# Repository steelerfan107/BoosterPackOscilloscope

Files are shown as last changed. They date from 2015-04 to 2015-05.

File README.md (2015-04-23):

# BoosterPackOscilliscope
An open hardware design sponsored by Texas Instruments to create a Oscilloscope BoosterPack for their LaunchPad series.

#Results

YouTube Videos of Current Version

https://www.youtube.com/watch?v=cYiwDeTmkGY
https://www.youtube.com/watch?v=qeyE9i_el2E
https://www.youtube.com/watch?v=waJ3gXQC8M0
https://www.youtube.com/watch?v=UX_YCJf1Lo4

#Design Files

Contains 
	- Software Files including the Energia Workspace and the Modified Screen Drivers
	- Hardware Files containing EAGLE files of the schematic and board designs. Also included are seperate sheets showing each subsystem.
	- BOM - Bill of Materials

#Reports

Contains
	- All of the reports for this project including
		Project Proposal - Initial project definition 
		Project Plan 	 - Initial schedule of project completeion 
		Decomposition 	 - A breakdown of each subsystem into circuits explaining why parts were used and how
		Final Reort	 - Outlines what worked well and what didnt

#Reserch Memos

Contains
	- Three memos looking into differant aspects of the project.

#Technical Sources

Contains
	- Datasheets of all major parts used

#Testing Plans and Data

Contains
	- Plans to test two subsystems and the results

#User Manual 
	- Contains how to setup project once the board is assembled and fabricated 

If you have any questions just email me at: eric.taylor.9090@gmail.com

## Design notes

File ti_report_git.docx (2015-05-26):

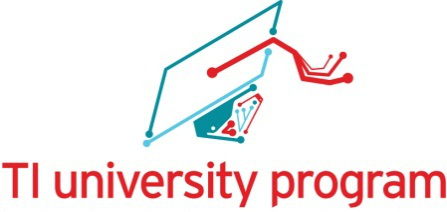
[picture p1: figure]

Oscilloscope BoosterPack (Low Cost) | Rose-Hulman

TI Innovation Challenge 2015 Project Report

Team Leader: | | Eric Taylor, taylorem@rose-hulman.edu
Team Members: | | Team Raymond Montgomery, montgora@rose-hulman.edu
Advising Professor: | | Mark Yoder, yoder@rose-hulman.edu
Video | | https://www.youtube.com/watch?v=cYiwDeTmkGY
Texas Instruments Mentor (if applicable): | | Trey German,treygerman@ti.com
Date: | | 5/11/2015
Qty. | List all TI analog IC and TI processor part number and URL | | 1) Explain where it was used in the project? 2) What specific features or performance made this component well-suited to the design?
2 | THS4121 | | This part was used for the Single-To-Differential conversion on the front end. Two were needed to get two channels. This was well suited because it ran of 3.3V and had the proper input range for the inputted signal and an adjustable common mode voltage to match with the LMH6882’s common mode voltage.
1 | LMH6882 | | This was used to have programmable gain on both of the channels. This was used because it has two channels on a single chip and had a wide range of gain settings which is useful for our application. The parallel bus also made it easy to control.
2 | OPA140 | | These were used to buffer the common mode voltage coming out of the ADC into the THS4121 and LMH6880. These were used because of the proper input range and we just were looking for the cheapest general purpose op amp possible since no frequency specs were needed.
1 | ADS5237 | | This was the ADC of the circuit used to sample both of the channels. It was used because of the fast sample rate of 65 MSPS and having a high 10 bit resolution. The 65 MSPS was around the limits of the EPI, and 10 bits was about our target when designing the front end. (Any more precision would be lost in the quality of the front end)
1 | TM4C1294NCPDT | | This was the microcontroller used to control our project. Since we are making a BoosterPack designed to attach to a Launchpad we picked the Connected LaunchPad because of the large amount of Pins and EPI bus capability,
3 | OPA890 | | These were used as an amp to offset the triggering signal and as a comparator to compare the signal to a specific trigger level. These chips were selected because of the low amount of skew and fast switching capabilities.
1 | TL7660 | | This was used as a negative source for the triggering circuit. This part was used because it was the cheapest part that did the intended job.

  - https://www.youtube.com/watch?v=waJ3gXQC8M0
  - https://www.youtube.com/watch?v=UX_YCJf1Lo4 https://www.youtube.com/watch?v=qeyE9i_el2E

GitHub: https://github.com/steelerfan107/BoosterPackOscilloscope

Project abstract (a short high level written description of the design and motivation behind project), 1,000 words max:

This project's objective was to design an oscilloscope BoosterPack that is compatible with TI LaunchPad series that is a low cost alternative to the typical desktop oscilloscope. This project was open source so anyone can learn from the hardware and software design and be able to expand upon them. The final product must be able to function as a reliable oscilloscope at an affordable cost to both hobbyists and students. As a low end design, the oscilloscope BoosterPack needs to push its cost down as much as possible while having the features of a typical oscilloscope. The main goal was to create a BoosterPack that has two measurement channels that can take a +/- 15V signal and has a bandwidth of 7MHz for under $50.

The design of this project had many aspects involving hardware and software. The hardware design consisted of three main circuits that we would need to design: sampling, front end, and triggering. The front end consisted of single to differential conversion along with adjustable gain to go into the sampling circuit. The sampling circuit consisted of an ADC to sample the signal from the front end and send it to the microcontroller. Finally the triggering circuit which takes a signal from the front end and compared it to a set level adjusted by the user and tells the microcontroller when to start sampling. All of this hardware will be on one board that is BoosterPack compatible and can be attached to the Connected LaunchPad. This allows for a display to be attached on top of this BoosterPack to display the signals. For this specific project we used a premade LCD BoosterPack and SPI controllers.

The other aspect was the software to control the device. For this we used Energia for the development and contained four parts. The first part was voltage and time deviation control. This was just done using the on board LaunchPad user buttons. The next was the amplifier control which was also just GPIO control. The next was the display drivers which were adapted from C drivers that came with the premade BoosterPack. Finally the sampling control with consisted of EPI, uDMA, and some other general code. The EPI was used to read in the 20 bit (both channels) quickly and the uDMA was used to store them in memory. Then two buffers were made to store the split samples and to determine if a certain samples changed positions on screen to keep screen refreshing to a minimum. However for our project we could not get the uDMA to work so we used timer interrupts to control how fast we took in samples. This greatly reduced the bandwidth of what we could measure, but since this project is open source and on GitHub there is the opportunity to add this feature in later.

## Table of Contents

## List of Tables and Figures

Figure 1. Primary Stakeholders and Features………………………………………………………………………………5

Figure 2. Domain Diagram ………………………………………………………………………………………………………….6

Figure 3. Logical Architecture………………………………………………………………………………………………………7

Figure 4. Front End Subsystem…………………………………………………………………………………………………….8

Figure 5. Trigger Level Subsystem………………………………………………………………………………………………..9

Figure 6. Sampling Subsystem……………………………………………………………………………………………………...9

Figure 7. Software Subsystem……………………………………………………………………………………………………..10

Figure 8. 50mV sine at (100kHz, 1MHz, 10MHz) (Top – Input to PGA, Bottom – Output of PGA).. 11

## Project Description

The project was to create an oscilloscope BoosterPack for TI’s Launchpad series which had the following features: two measurement channels, hardware triggering, user control, 6.5 MHz bandwidth, and +/ 15V input swing for all under $50. The reasoning behind the selection of these features can be seen below. In our final product we were able to accomplish most of what was needed but not all. The BoosterPack did have two working channels and a hardware trigger for under $50, however the software could not sample fast enough to get the 6.5 MHz bandwidth and adjustments are needed on the front end to get a full +/- 15 V input swing. The final board we made had a 200 kHz bandwidth and +/- 1.5V input swing.

2.1 Description of the Primary Stakeholders and Features

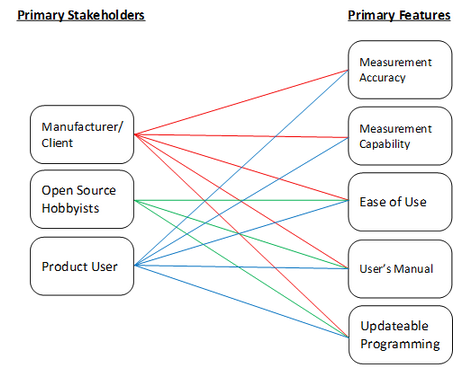
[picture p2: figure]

Figure 1. Primary Stakeholders and Features

The final product which consists of our physical circuit, the code that runs it, and the open source material all of which are determined by the primary stakeholders and features of our system as seen in Figure 1. The client, TI, provided this project submission and therefore cares about all the deliverables they requested. Anyone who uses the oscilloscope BoosterPack wants a functional final product and would want to reference the open source material for debugging errors and exploring the design of the product. Those who do own the product (like hobbyists and other recreational researchers) can still view the open source materials for studying circuit and code designs. The remaining features describe the actual function of the oscilloscope BoosterPack. ‘Measurement Accuracy’ and ‘Measurement Capability’ are distinct and necessary features for the final product. The accuracy describes the how well the oscilloscope BoosterPack’s measurements are to the actual signal being measured, while capability is a necessary step in determining signal accuracy because we need confirm that the data displayed on the oscilloscope is measurement data. Since the program on the circuit’s microcontroller can be changed, the user can see how making changes to the program can affect the operation of the oscilloscope and other programs can be loaded onto the LaunchPad so it can be used for different projects. As the project becomes easier to use, the user enjoys using the oscilloscope BoosterPack more which is why ease of use is a primary feature.

2.2 Description of the Solution

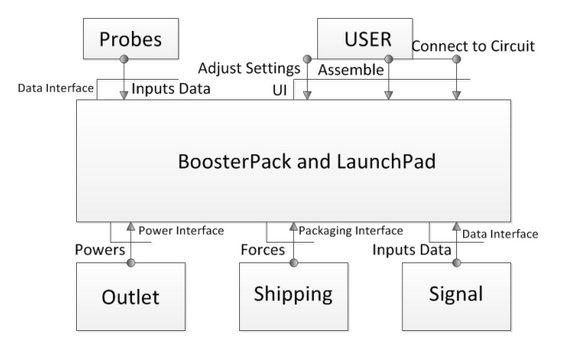
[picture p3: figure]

Figure 2. Domain Diagram

In Figure 2 the domain model of the project is presented. In this model the outside actors of the system are identified along with their interactions with the system. The first actor are the probes that are used in conjunction with the system. This directly related to measurement accuracy, ease of use, price limit, and measurement capabilities. The probes are what connects the signal to the circuit and have characteristics like input impedance and signal attenuation. These can effect what type of signal that could be measured and how accurate the system can be. The probes are also a separate component to reduce cost of the final package, and the user can use ones to their specification. For the final board design any BNC probe could be attached to measure signals. However when the 10x setting is used the signal does not go through. Further research is needed to figure out why this happens.

The next outside actor is the user which adjusts the settings, assembles/updates, and in general uses the scope. This directly relates to the ease of use, instruction manual, measurement capabilities, and price limit. The user needs to be able to operate the scope with ease, and should have a similar interface to other scopes on the market. This coincides with the user manual which explains the use of the scope to the user. Finally the user wants to be able to buy the product at a reasonable price given the performance the scope has. This was satisfied using buttons that came attached to the LaunchPad and a potentiometer attached to the BoosterPack. These controls allowed the user to adjust time and voltage per deviation, and also adjust the trigger level. Using controls that came with the LaunchPad also reduced the total cost of the board.

The next outside actors are outlet which directly effects power consumption, shipping which involves how the product is packaged, and the signal which related to accuracy and capability. The outlet determines how much power the scope can use. For power the final board can be powered by any micro usb source including portable battery packs. The shipping of the product relates the manufacturability and how the product is packaged. This was accounted for in the hardware design of the board. Finally the signal shape, size, and characteristics need to be known so the scope can be made to measure the variety of signals that it needs.

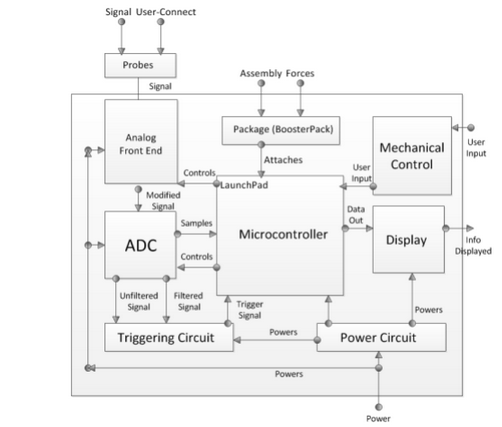
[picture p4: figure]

Figure 3. Logical Architecture

In Figure 3 we see the logical architecture of the system which describes how the scope will respond to the outside actors and shows how the system will function in general. Following the flow of the signal first comes the analog front end which accepts the signal from the scopes and proceeds to attenuate/amplify the signal, apply the proper common mode voltage, and make it differential. The signal is also put through a filter to reduce high frequency noise. The signal then proceeds to the ADC where it is sampled and then read into the memory of the microcontroller. The microcontroller the uses these samples and based on the user input displays the signal on a LCD screen.

The front end involves many parts, first of which is the THS4121 which does the single to differential conversion. This part was a cheap general part that is able to handle +/- 1.5V swings which was appropriate because we planned 10x probes working with the board which they did not. With 10x probes the +/- 1.5V swing would be enough for a +/- 15V input. This part also had the necessary bandwidth to handle 10 MHz signals.

The next part used was the programmable gain amplifier, LMH 6882. This part was first suggested by the client and worked well for our purpose. This amplifier has up to 25dB gain allowing for the measurement of small signals. This part also had two channels which reduced the part count on the board reducing cost.

Next came the sampling system or ADC. The ADC chosen was the ADS5237. This part had a sampling rate of 65 MSPS which allowed the measurement of signals up to 7MHz assuming the industry guideline of having 10 samples per period to have a good measurement on a signal. It also was selected because it had two channels which reduced part count and was relatively cheap compared to other ADCs that were up for consideration. Finally it had 10-bits of resolution which the client stated he wanted in the planning process.

The microcontroller which takes in the samples was satisfied using the Tiva C connected LaunchPad from TI. This board was needed because of the extra pins that were included which were needed to satisfy all of the requirements. This board also had EPI (External Peripheral Interface) which was a parallel bus that was needed to receive the 20-bit data signal for both channels at appropriate speeds.

Other blocks include the triggering circuit which takes in the filtered and unfiltered signal and tells the microcontroller when to start sampling based on a desired trigger level. This was done using cheap general purpose op-amps because of their low cost, and had satisfactory bandwidth for our features. The power circuit takes in the power from the outlet or USB and provides the microcontroller and the circuit with power. The power circuit was on the LaunchPad itself and no further circuitry was needed. The package block includes how it has to be manufactured to be able to interact with the Launchpad. This will be done by following BoosterPack templates and specifications. Finally the mechanical control which includes buttons which are on the Launchpad and a potentiometer which is on the BoosterPack.

Finally the display requirement was satisfied by an external BoosterPack made by a third party. This allowed us to focus on other features while satisfying a requirement at low cost. A simple 2.2” LCD controlled by SPI was used because of its low cost and simplicity to control.

This solution is able to deal with all of the major features which includes measurement accuracy, ease of use, measurement capabilities, updateable programming, and user manual. The measurement accuracy and capabilities are determined by the front end and ADC. Ease of use is taken care of by the mechanical control, display, and probes. However it couldn’t fully handle the features because the software wasn’t able to take in samples fast enough. The hardware could handle this requirement but software could not. Other than this detail the hardware selected was able to satisfy all of the requirements

## Hardware Design

### Front End

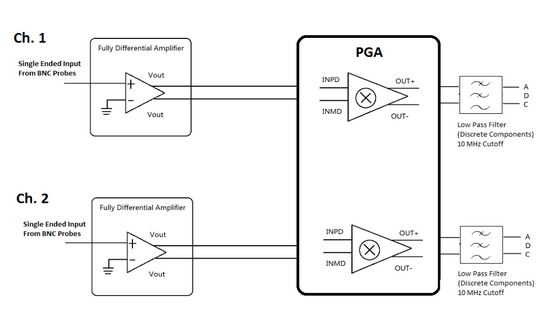
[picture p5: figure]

Figure 4. Front End Subsystem

For the Analog Front End, there is a BNC probe inputting the single ended signal. The reason we want the probes is to attenuate the signal by 10x and give the input impedance of 1MOhm. This is done because looking into the buffer there is a known high impedance of 1 Mohm and known attenuation.

Next, we have a fully differential amplifier (THS4121). Because the programmable differential amplifier requires two differential inputs, so we use the THS4121 to transfer the single signal to two differential input signals.

Last we have the dual channel differential PGA (LMH6882). The PGA Amplifies small signals so the ADC can measure the signals with proper resolution. This PGA is controlled by the microcontroller through parallel logic telling how much gain the signal need.

Finally there is a low pass filter to get rid of any noise to the ADC with a cutoff frequency of about 10 MHz.

### Triggering Circuit

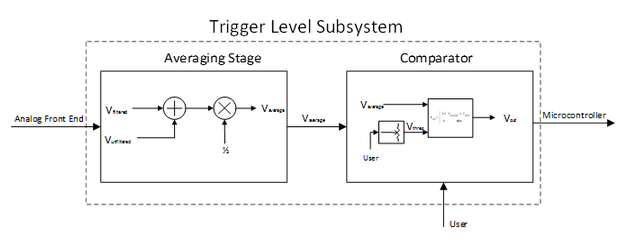
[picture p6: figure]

Figure 5. Trigger Level Subsystem

After a channel receives a signal. The Analog Front End scales the signal down so the op-amps in the Triggering Circuit can manipulate the input signal within the supply voltages. The user controls the potentiometer with a knob, or a similar control structure. The output of the Triggering Circuit is an array of logical values based on the sampling rate of the microcontroller and if there is one logical high in the array then the waveform is displayed. Logical high is an output of 5V and a logical low is an output of 0V

### Sampling Subsystem

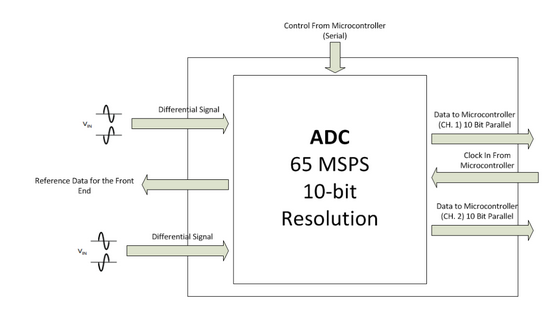
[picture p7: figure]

Figure 6. Sampling Subsystem

For our circuit we are going to use the ADS5237 ADC from TI. This chip is a dual channel, 10-bit resolution ADC that can sample at 65 MSPS. This will enable us to measure signals up to 6.5 MHz. This part has a listed use case for test equipment so that also gives reassurance it would be good to use in this case. The chip requires a clock signal from the microcontroller to tell it when to sample, and the data is sent back to the microcontroller over two 10-bit parallel lines. The analog signal coming in comes from the ADC and needs to be a differential signal within 0 to 2 V peak to peak.

Our ADC will not need serial control for now so it is disabled in the schematic for now.

## Microcontroller and Software

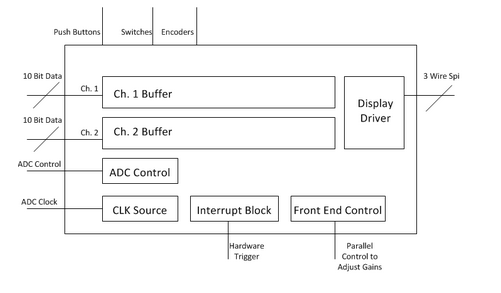
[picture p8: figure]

Figure 7. Software Subsystem

The microcontroller is the center of the project and will hold all of the software. We are using the Tiva C microcontroller that comes on the Connected series of Launchpad. The microcontroller is responsible for taking in the sampled data through an EPI (External Peripheral Interface) bus and storing it into a buffer after the trigger interrupts the microcontroller.

Knowing things such as voltage per division and time per division shown on the screen it will also control the sampling rate through increasing/decreasing the clock frequency to the ADCs. It will also control the amplification through the programmable gain amplifier which is a simple parallel interface.

The microcontroller also takes the user input from mechanical controls such as the push button, rotary encoders, and slide switches, and displays data on a LCD display which it will connect to through the built in SPI drivers.

### Testing Methids

Much of the formal testing of the project involved testing spate subsystems of the project. The first subsystem tested was the analog front end which was our black box testing.

For the black box testing we wanted to confirm the input requirements to the scope. This includes features like how high frequency of a signal can be inputted to the scope, and how large of a signal. This testing revolved around the front end because that is what takes the input signal and delivers it to the ADC for sampling.

For the setup of this testing the final board was made so a scope probe can take an input signal and there were testing wires soldered to the output of the analog front end right before the ADC. This allows us to see when a certain signal is inputted that the signal gets to the ADC correctly to be sampled. Here we are mostly looking for shape because depending on the settings of the programmable gain amplifier the true amplitude is unknown and is only known to the microcontroller which provide the correct gain factor to the samples. For the sake of this testing the lowest settings of gain were used for the programmable gain amplifier.

To start testing the functionality was confirmed with a 50mV input which is reality simulates a .5 V input because of the 10x probes (probes used were set at 1X). At 50 mV a sine wave was put through at 1kHz, 100kHz, 1MHz, and 10 MHz in addition to a square wave at 1MHz and a ramp wave at 200kHz. Again here we want to confirm the correct shape going into the ADC.

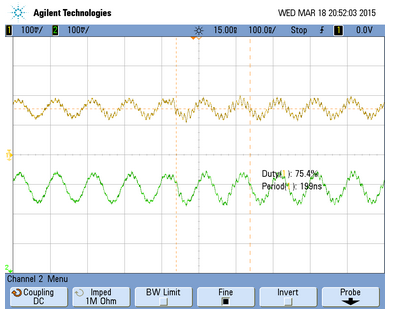
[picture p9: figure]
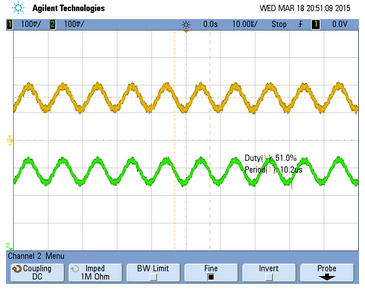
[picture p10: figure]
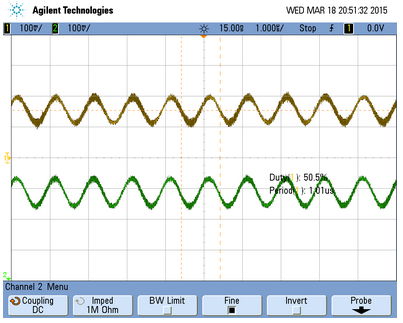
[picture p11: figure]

Figure 8. 50mV sine at (100kHz, 1MHz, 10MHz) (Top – Input to PGA, Bottom – Output of PGA)

Here is an example progression of the testing for the analog front end. In the above figure we specifically looked at small signals going into the front end and looking at what the ADC would see. Many configurations of this test were done at different frequencies and shapes but showing all would take too much space. Alongside this test our group also tested the triggering circuit individually.

For full system testing we assembled the oscilloscope and used it like anybody else would. We testing different shape, sizes, and frequencies of signals going into the scope. When we inputted a signal we tested what the screen was displaying. Many of these tests can be seen in the video and typically involved visual testing. Since our group ran out of time to finish the project in its entire little formal testing was done on the final system, it was mostly visual and user tested. The testing did go over well and showed what we got done worked, however it also did show what could be added to this project to make it better and where the shortcoming were. In the end we were able to input a +/- 1.5V signal up to 200 kHz, both channels were working, had adjustable voltage/time scaling, and had an adjustable hardware trigger. Fixes and further steps could be seen in the recommendations section.

### Conclusions

In the end our group was able to get the core functionality working along with many features such as the controllable trigger level and adjustable time/voltage scaling. It did fall short of the expected goals however. The Brightside is that small additions to software such as uDMA will improve the sampling speed, and addition of a selectable attenuator could improve input amplitude range.

### Future Work

Our project has fallen short of its expectations and its goals. The hardware is capable of handling the range of input signals (frequencies up to 7MHz) but the software can’t handle samples fast enough. A micro DMA method in software would help to handle samples faster and enables the oscilloscope BoosterPack to appropriately handle and display the higher frequency signals by writing the samples directly to memory when they are received. The software also doesn’t dynamically change the gain of the PGA to amplify smaller signals. However the control signals to do so are in hardware. More software would have to be added to allow the oscilloscope BoosterPack to measure the range of signals that we designed for. Finally adding a selectable attenuator to the front end would allow the hardware to accept larger signals. These recommendations would help the project to better meet the stakeholder features for Measurement Accuracy. Overall the core functionality works, meeting the Measurement Capability, Open Source Material, Ease of Use, and Updateable Programming features, but adding more software would allow the board achieve all its goals, and adding some hardware and software could help the project to meet these goals.

### Resources and Bibliography

Annotated List of Research Memos

[1] Yaohui Wang, Research of Analog Front End Design. October 7, 2014.

Description of the purpose and operation of an analog front end and looked into characteristics our group should look at when making our analog front end.

[2] Eric Taylor, Hold-Off Triggering, September 28, 2014.

A description of what hold off triggering is and how it works. This provided understanding of an oscilloscope feature that could be put into the scope at a later date.

[3] Raymond Montgomery, Oscilloscope Triggering. October 15, 2014.

This provided research into how our project will handle the triggering in hardware and gave understanding into which parts we should use and the general circuit subsystem that had to be made. This deals more with triggering hardware whereas the previous memo is software triggering features.

Annotated Biblliography

[1] I. King , High Performance Analog Front Ends, Analog Edge, Vol. IV Issue 1.

This source was used when the group didn’t have a good understanding of the purpose of an analog front end, and what characteristics of one made it a high performing one. This provided characteristics for the analog front end that our group could shoot for and design around.

[2] Microchip Technology Inc. Non-Inverting Summing Amps August 25, 2014. [Online]

This webpage explains the operation of amplifier circuits that sum signals together. This is useful in the triggering circuit to sum together the filtered and unfiltered signals.

[3] Circuits Today. Voltage Comparator. November 25, 2011. [Online]

This article was used to explain the user of voltage comparator circuits used in the triggering subsystem of our design.

[4] EEVBlog. Oscilliscope Trigger Holdoff Tutorial. March 29, 2011. #159 [Online]

This video provided understanding of holdoff triggering and how we could add it as a feature in our final scope.

[5] Texas Instruments. Oscilloscope Solution. [Online]

This is a compilation of resources by Texas Instruments that describes solutions and systems needed to make an oscilloscope. This was useful to learn all the systems we needed for our final project.

## Appendix

Note: All files and code on GitHub at steelerfan107/BoosterPackOscilloscope under Design Files

### Critical IC BOM

Part Value Device Package

-5V_SUPPLY TL7660_D_8 TL7660_D_8 D8

AVERAGER OPA890_DBV_6 OPA890_DBV_6 DBV6

COMPARATOR OPA890_DBV_6 OPA890_DBV_6 DBV6

OFFSET OPA890_DBV_6 OPA890_DBV_6 DBV6

U$3 LMH6882 LMH6882 WQFN-36-NJK

U1 ADS5237_PAG_64 ADS5237_PAG_64 PAG64

U2 THS4121_D_8 THS4121_D_8 D8

U3 THS4121_D_8 THS4121_D_8 D8

U4 OPA140AID OPA140AID SOIC127P600X175-8N 11MHz JFET Op Amp

U5 OPA140AID OPA140AID SOIC127P600X175-8N 11MHz JFET Op Amp

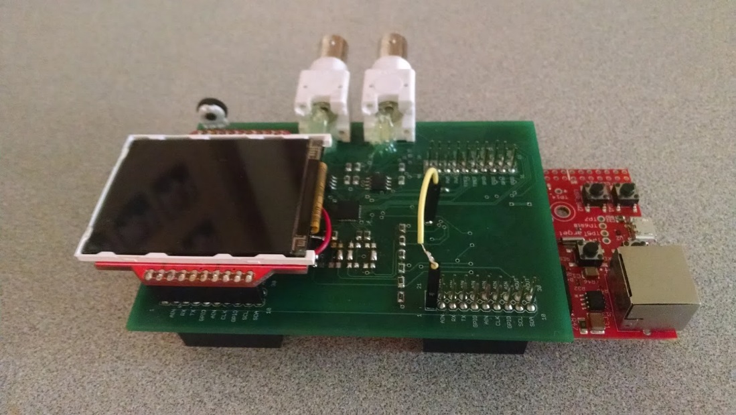
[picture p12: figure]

# TI BoosterPack Oscilloscope

User Manual 1.0

Eric Taylor and Raymond Montgomery | Rose-Hulman | Texas Instruments | Spring 2015

# Purpose

The purpose of this user manual is to help you get started setting up and getting familiar with the project. This assumes that you have the board already constructed from the board files on GitHub using the BOM also on GitHub. This will also include how to improve upon this project and traverse the files on GitHub .

# Table of Contents

Hardware Set-Up 3

- Color LCD Modifications 3
- Oscilloscope Board Jumper and Passive Filter 3
- Tiva C Connected LaunchPad 4

Software Setup 4

Usage of the Scope 5

TODOs 5

GitHub 5

# 1.0 Hardware Set-Up

To set up the hardware you need three things:

  - 2.2" Color LCD BoosterPack Kit by RobG
  - A Fabricated and Populated Oscilloscope PCB
  - Tiva C Connected LaunchPad

## 1.1 Color LCD Modifications

To make use of the EPI interface a small modification had to be made to the LCD BoosterPack hardware. You have to make sure neither jumper is soldered on the D/C pin, and then attach a wire to the middle pad and connect it to pad JP5. A picture showing this is below.

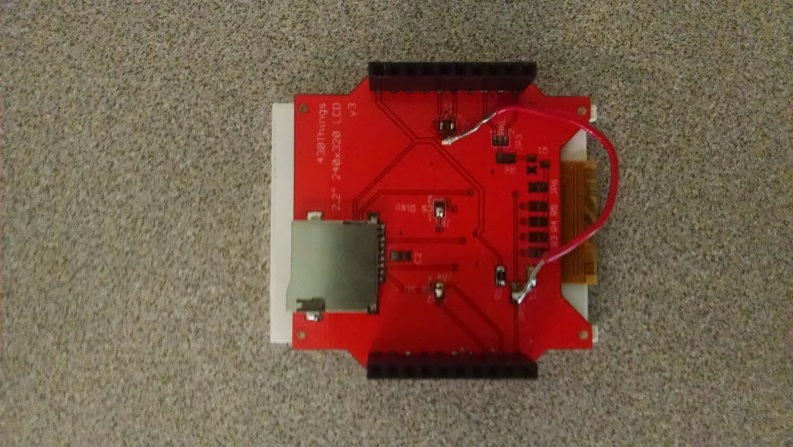
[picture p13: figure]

## 1.2 Oscilloscope Board Jumper and Passive Filter

For the purposes of debugging a pin was left exposed on the ADC for this first revision. Next revisions should connect this pin to the standard LDD for the ADC. (Connect VDRV to VDD in the EAGLE files). This jumper is necessary to power the ADC. A typical female-to-female jumper was used. A picture showing it is seen below. (The Yellow Wire). Also leave passive filter disconnected and solder the cap connections so the signal can continue through. More explanation in TODO.

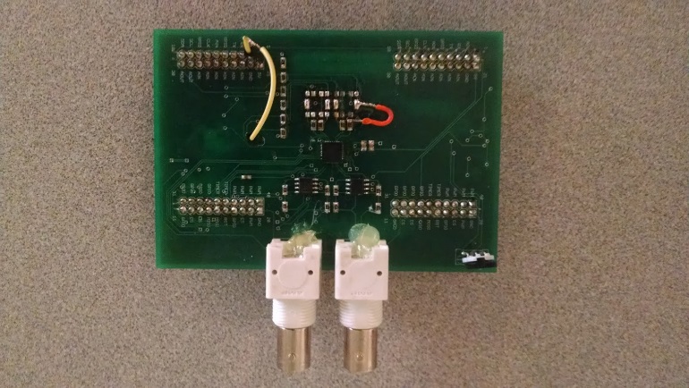
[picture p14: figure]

*Note - Orange Wire is there because of mistake while soldering

## 1.3 Tiva C Connected LaunchPad

No modifications should be needed. Make sure jumpers are connected like below.

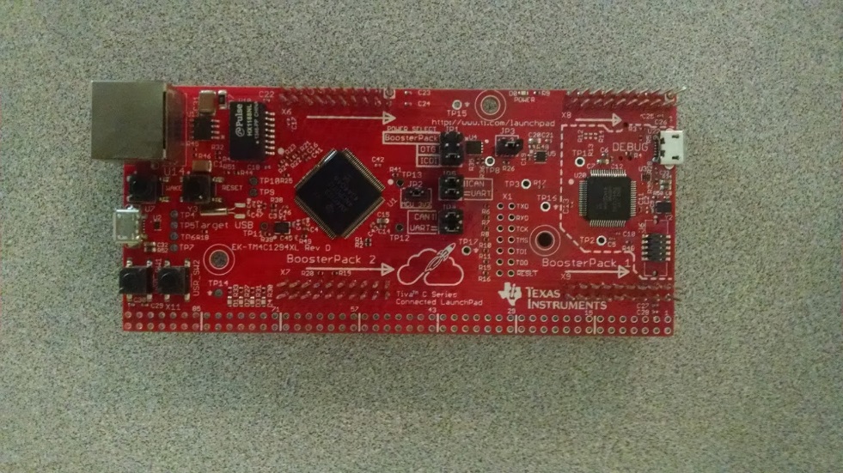
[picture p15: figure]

Once all hardware is setup, you can attach all of the pieces as seen on the first page.

# 2.0 Software Setup

Four things are needed for the software setup.

  - Energia w/ Tiva C Drivers
  - Senior_Project_Main.ino (on GitHub under Software Code)
  - Screen_ILI9340_Library.cpp/h

Minimal Setup is needed. First download Energia and put the screen driver and header files in the following path. (Note: The drivers are edited from the original online to account for the one pin being moved across the board.)

..\energia-0101E0013\hardware\lm4f\libraries\

Then open Senior_Project_Main.ino and select Tiva C tm4c129 as the board, Finally compile and run.

# 3.0 Usage of the Scope

  1. To use the scope you can use any BNC connector or 1x probe. However 10x probes did not work when tested with the system. Connect probes up like a typical scope. For this revision you can only trigger of one channel. (BNC away from Screen).
  2. Only signals from +/- 1.5 can be inputted at the end of the probe.
  3. Power can be supplied through any micro USB source. Portable battery or laptop will work.
  4. The trigger level can be adjusted using the potentiometer. Then the voltage per deviation and time per deviation can be adjusted using the two user buttons on the LaunchPad.

Note: The GUI is still in its early stages and can be improved upon.

# 4.0 TODOs

This section contains improvements that can be made on this project and steps to continue its development.

  1. Switch BNC connections so that they are vertical. They are currently unstable.
  2. Add buffer to front end so that 10x probes cannot load circuit.
  3. Add switchable attenuator to front end.
  4. Add uDMA to software to collect samples faster and be able to achieve full 7 MHz bandwidth . Currently a timer interrupt is used and the bandwidth is about 200kHz.
  5. Put 10MHz flat pass band active filter instead of current passive filter.

# 5.0 GitHub

On GitHub you can find a directory listing on the front page giving explanation to the file directory and source files. GitHub at steelerfan107/BoosterPackOscilloscope

### Schematics

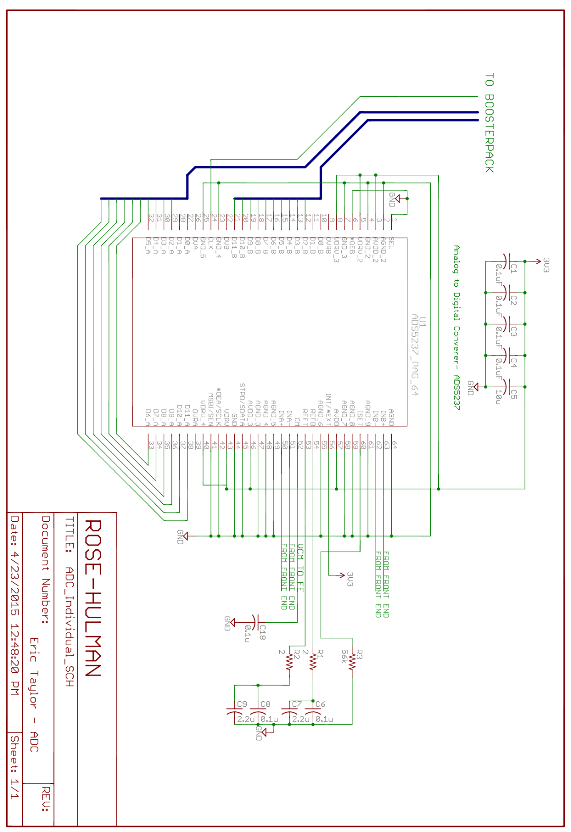
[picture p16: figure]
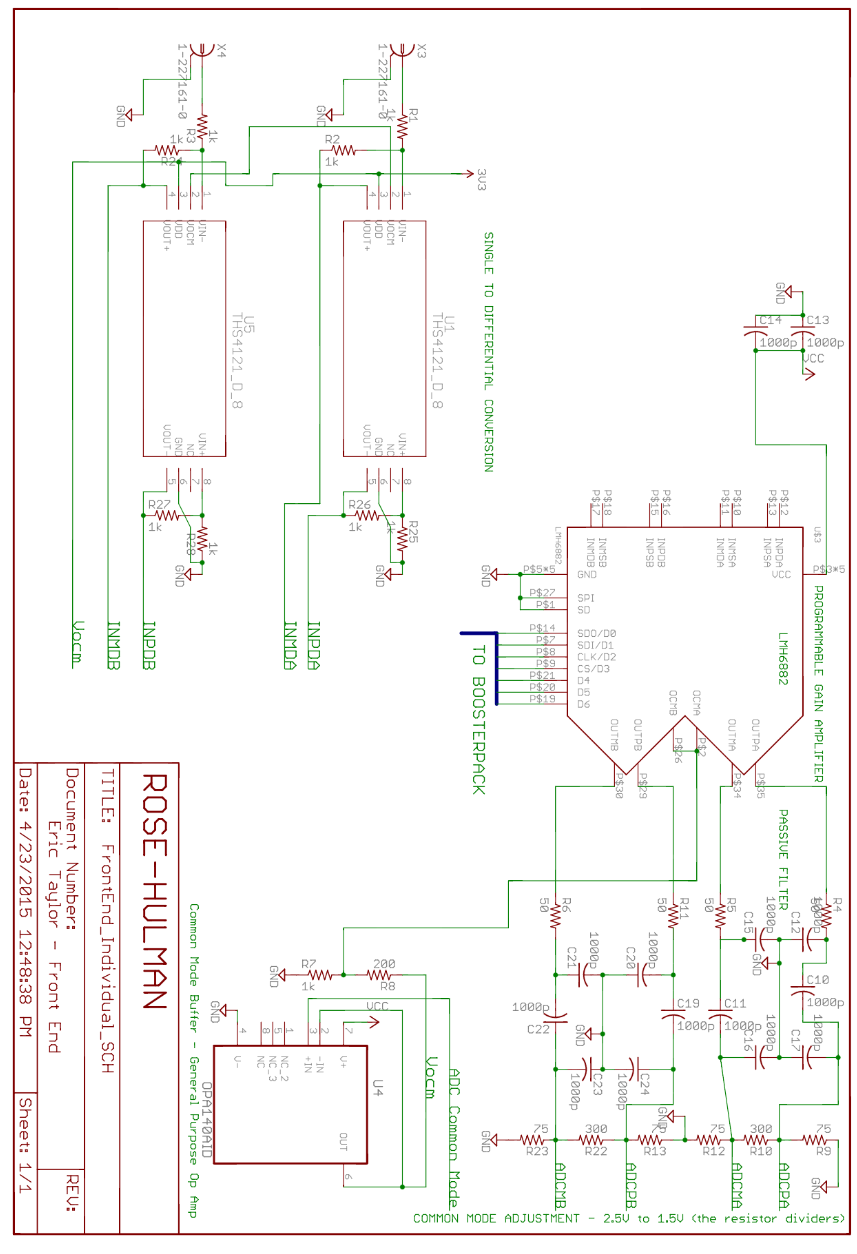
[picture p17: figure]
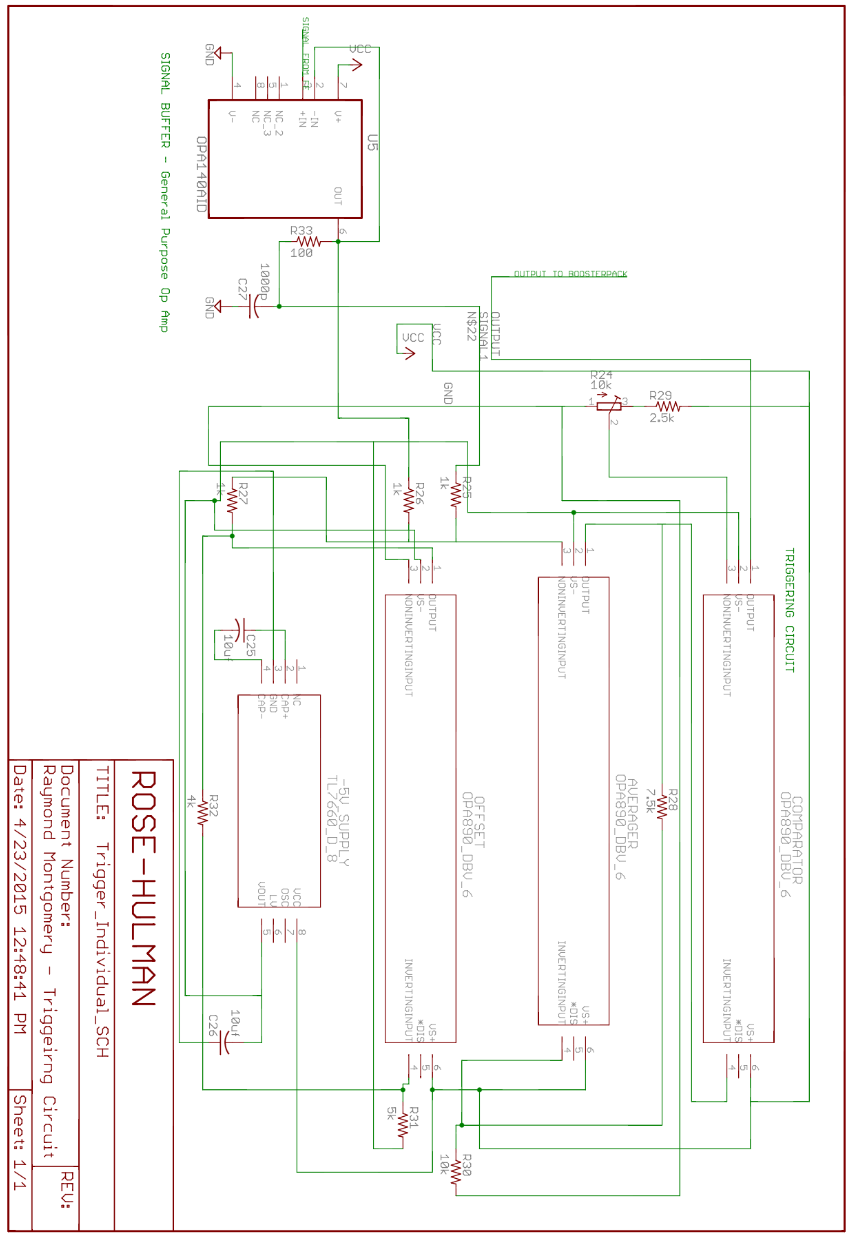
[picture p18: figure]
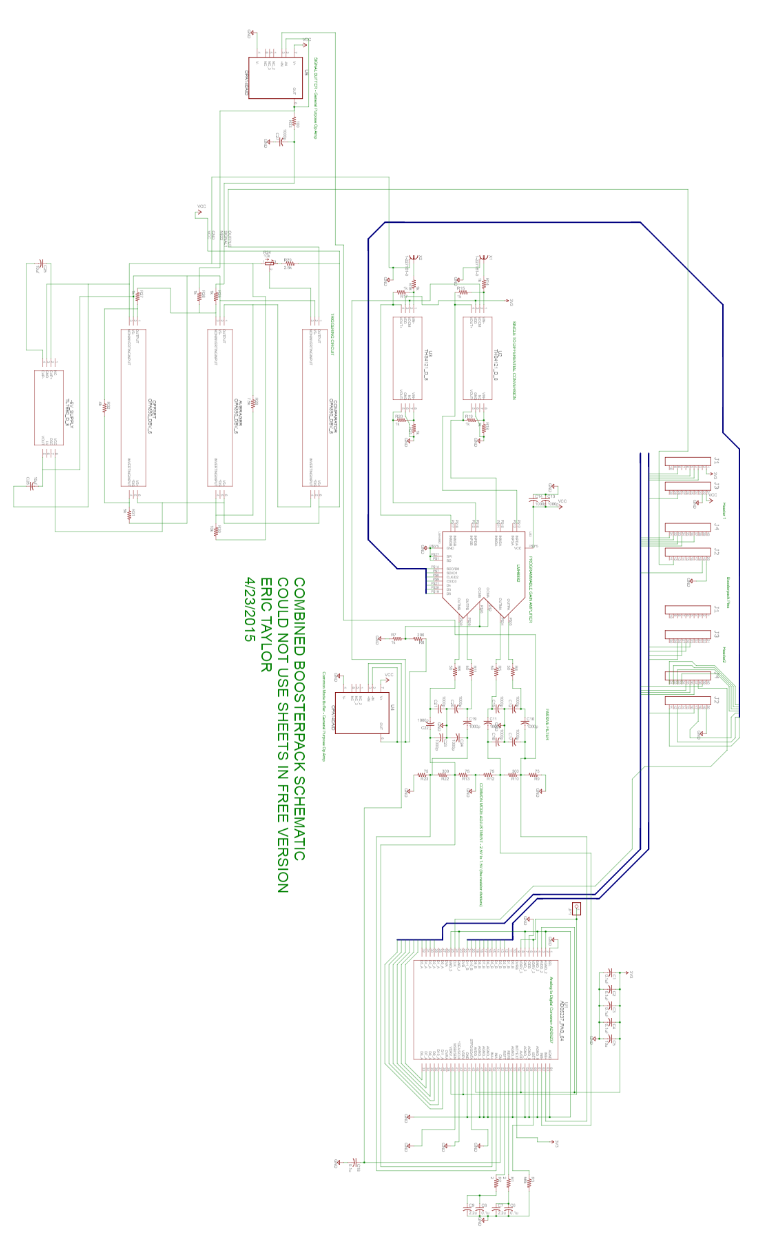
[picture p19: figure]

### Board File

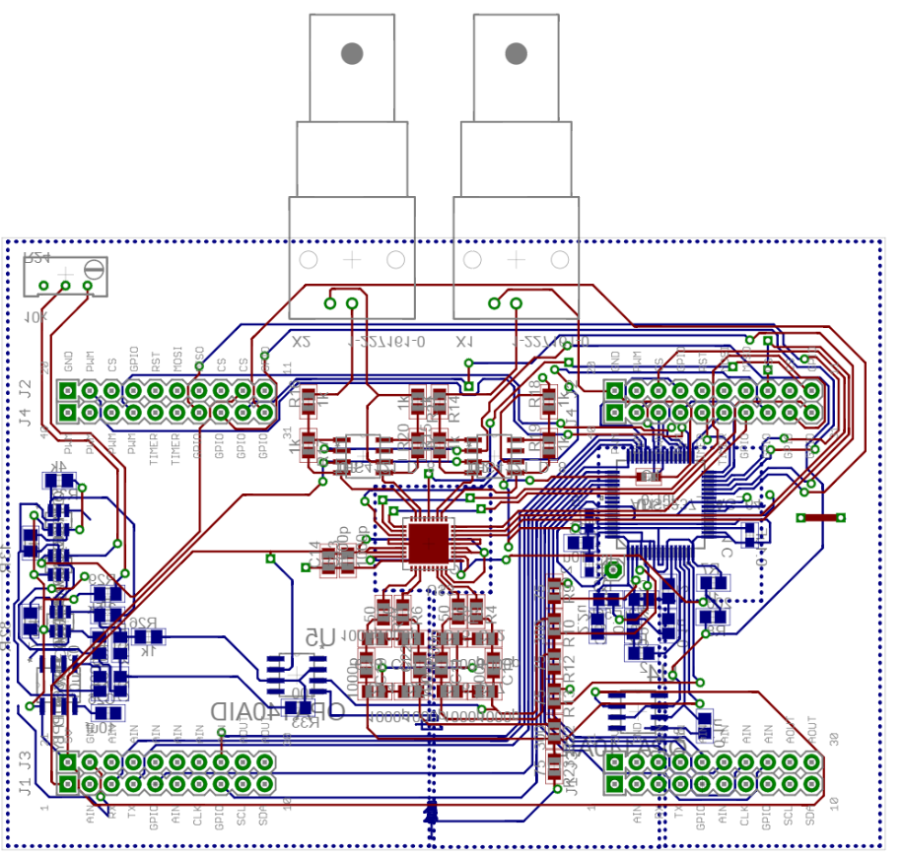
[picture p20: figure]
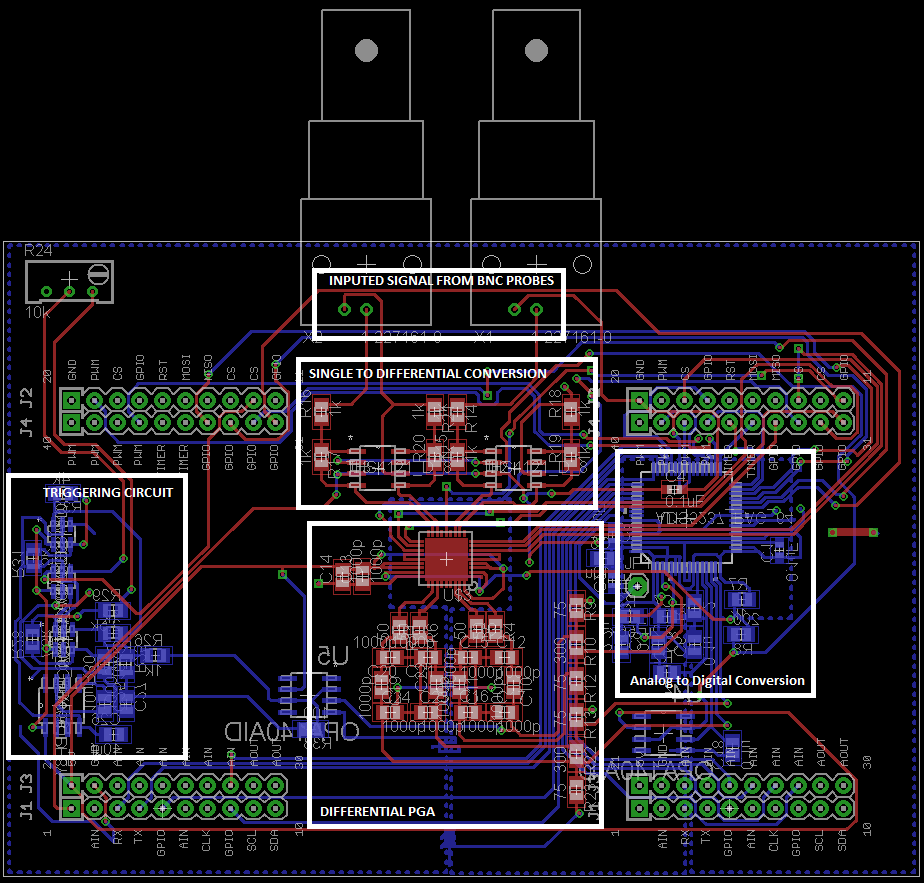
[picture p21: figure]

### Gerber Files

#### Top

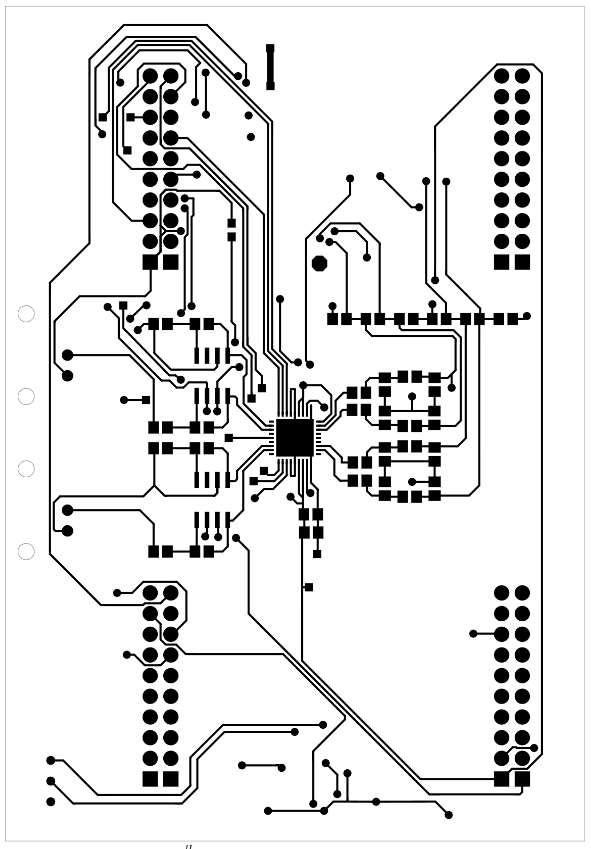
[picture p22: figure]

#### Bottom

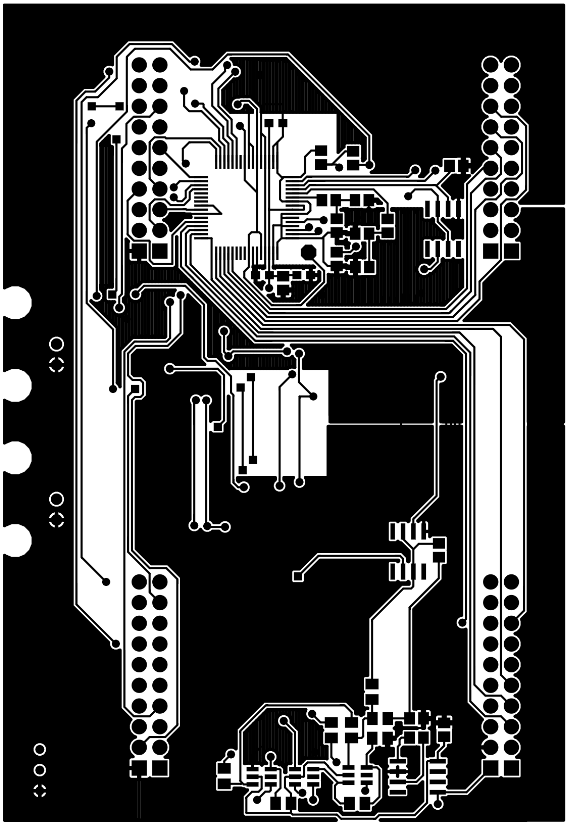
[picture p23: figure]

### Code

// Eric Taylor

// Rose-Hulman - ECE 462 Senior Design

// TI BoosterPack Oscilliscope Software

//

// This program uses an EPI interface to read in 20 bit samples (First 10 bits - Channel 1, Second 10 bits - Channel 2)

// and uses a timer interupt to have a constant time between samples. These samples are then shown on a LCD screen using

// a SPI controller.

//

// The following code was mide by me with exception of the SPI driver for the LCD included in "Screen_ILI9340_Library.h"

//

// TODO: Setup uDMA so sample can be read in faster allowing faster signals to be measured.

/////////////////////////////////////////

// Header Files

////////////////////////////////////////

#include "Energia.h"

// Include application, user and local libraries

#include "SPI.h"

#include "driverlib/epi.h"

#include "driverlib/udma.h"

#include "driverlib/gpio.h"

// Screen selection

#define ILI9340 // HX8353E K35 HI32 W32 ILI9225B HY28A ST7735 PicasoSPE PicasoSGC

#include <stdint.h>

#include <stdbool.h>

#include "inc/hw_types.h"

#include "inc/hw_memmap.h"

#include "inc/hw_gpio.h"

#include "driverlib/gpio.h"

#include "driverlib/rom.h"

#include "driverlib/sysctl.h"

#include "driverlib/timer.h"

#include "inc/hw_ints.h"

#include "driverlib/interrupt.h"

#if defined(ILI9340)

#include "Screen_ILI9340_Library.h"

Screen_ILI9340 myScreen;

#endif

////////////////////////////////////////////////////

// Global Variable Declarations

////////////////////////////////////////////////////

uint8_t largeOrientation = 0;

uint32_t data_location = 0;

int flag = 0, test = 0;

unsigned long * data_addr = (unsigned long *)0x60000000;

volatile int temp = 1;

volatile int tempB = 1;

signed long buffer_a[320],old_buffer_a[320];

signed long buffer_b[320],old_buffer_b[320];

unsigned long sample;

unsigned long int_sample;

/*

void * PP_BUFFER_A = 0;

void * PP_BUFFER_B = 0;

///////////////////////////////////////////////////

// DMA Setup (Not Used at the Moment)

//////////////////////////////////////////////////

tDMAControlTable g_dmaCtrl[64] __attribute__ ((aligned(1024)));

void setupDMA(){

PP_BUFFER_A = (void *)malloc(32*1024);

PP_BUFFER_B = (void *)malloc(32*1024);

SysCtlPeripheralEnable(SYSCTL_PERIPH_UDMA);

uDMAEnable();

uDMAControlBaseSet(g_dmaCtrl);

uDMAChannelAssign(UDMA_CH20_EPI0RX);

uDMAChannelSelectSecondary(UDMA_DEF_TMR1A_SEC_EPI0RX);

uDMAChannelAttributeEnable(UDMA_SEC_CHANNEL_EPI0RX, UDMA_ATTR_HIGH_PRIORITY);

uDMAChannelAttributeDisable(UDMA_SEC_CHANNEL_EPI0RX, UDMA_ATTR_USEBURST | UDMA_ATTR_REQMASK | UDMA_ATTR_ALTSELECT);

uDMAChannelControlSet(UDMA_CH20_EPI0RX | UDMA_PRI_SELECT,UDMA_SIZE_32 | UDMA_SRC_INC_NONE | UDMA_DST_INC_32 |UDMA_ARB_8);

uDMAChannelTransferSet(UDMA_CH20_EPI0RX | UDMA_PRI_SELECT,UDMA_MODE_PINGPONG,data_addr,PP_BUFFER_A,1023);

uDMAChannelControlSet(UDMA_CH20_EPI0RX | UDMA_ALT_SELECT,UDMA_SIZE_32 | UDMA_SRC_INC_NONE | UDMA_DST_INC_32 |UDMA_ARB_8);

uDMAChannelTransferSet(UDMA_CH20_EPI0RX | UDMA_ALT_SELECT,UDMA_MODE_PINGPONG,data_addr,PP_BUFFER_B,1024);

//uDMAIntRegister(UDMA_INT_SW, DMA_HandleInterrupt);

uDMAChannelEnable(UDMA_CH20_EPI0RX);

//uDMAChannelRequest(UDMA_SEC_CHANNEL_EPI0TX);

}

*/

///////////////////////////////////////////////////

// Setup Gain

// The pins in order control - D0, D1, D2, D3, D4, D5, D6 of the PGA. This sets up these pins to be output enabled.

///////////////////////////////////////////////////

void setupGain(){

pinMode(51, OUTPUT);

pinMode(53, OUTPUT);

pinMode(58, OUTPUT);

pinMode(74, OUTPUT);

pinMode(73, OUTPUT);

pinMode(72, OUTPUT);

pinMode(71, OUTPUT);

}

//////////////////////////////////////////////////

// Setup the External Periphrial Intrerface (EPI Interface Reads in Data From the ADC)

/////////////////////////////////////////////////

void setupEPI()

{

// Define what pins in each of the ports are used for the EPI

#define EPI_PORTA_PINS (GPIO_PIN_6 | GPIO_PIN_7)

#define EPI_PORTB_PINS (GPIO_PIN_3 | GPIO_PIN_2)

#define EPI_PORTC_PINS (GPIO_PIN_7 | GPIO_PIN_6 | GPIO_PIN_5 | GPIO_PIN_4 )

#define EPI_PORTG_PINS (GPIO_PIN_1 | GPIO_PIN_0 )

#define EPI_PORTK_PINS (GPIO_PIN_0 | GPIO_PIN_1 | GPIO_PIN_2 | GPIO_PIN_3 | GPIO_PIN_4 | GPIO_PIN_5)

#define EPI_PORTL_PINS (GPIO_PIN_0 | GPIO_PIN_1 | GPIO_PIN_2 | GPIO_PIN_3 | GPIO_PIN_4 | GPIO_PIN_5)

#define EPI_PORTM_PINS (GPIO_PIN_0 | GPIO_PIN_1 | GPIO_PIN_2 | GPIO_PIN_3)

#define EPI_PORTN_PINS (GPIO_PIN_2 | GPIO_PIN_4 | GPIO_PIN_5)

#define EPI_PORTQ_PINS (GPIO_PIN_0 | GPIO_PIN_1 | GPIO_PIN_2 | GPIO_PIN_3)

// Configuration options for the EPI

unsigned long ulEPIConfig = EPI_GPMODE_CLKPIN

| EPI_GPMODE_ASIZE_4 // address bus size of 4

| EPI_GPMODE_DSIZE_24 //

| EPI_GPMODE_READ2CYCLE // The RD2CYC bit in the EPIGPCFG register must be set at all times in General-Purpose

| EPI_GPMODE_FRAMEPIN; // frame signal

// Enable EPI0

SysCtlPeripheralEnable(SYSCTL_PERIPH_EPI0);

// SET GPIO to connect to Hardware

SysCtlPeripheralEnable(SYSCTL_PERIPH_GPIOA);

SysCtlPeripheralEnable(SYSCTL_PERIPH_GPIOB);

SysCtlPeripheralEnable(SYSCTL_PERIPH_GPIOC);

SysCtlPeripheralEnable(SYSCTL_PERIPH_GPIOG);

SysCtlPeripheralEnable(SYSCTL_PERIPH_GPIOH);

SysCtlPeripheralEnable(SYSCTL_PERIPH_GPIOK);

SysCtlPeripheralEnable(SYSCTL_PERIPH_GPIOL);

SysCtlPeripheralEnable(SYSCTL_PERIPH_GPIOM);

SysCtlPeripheralEnable(SYSCTL_PERIPH_GPION);

SysCtlPeripheralEnable(SYSCTL_PERIPH_GPIOP);

SysCtlPeripheralEnable(SYSCTL_PERIPH_GPIOQ);

//Configure Pins to drive 8mA

GPIOPinConfigure(GPIO_PK0_EPI0S0);

GPIOPinConfigure(GPIO_PK1_EPI0S1);

GPIOPinConfigure(GPIO_PK2_EPI0S2);

GPIOPinConfigure(GPIO_PK3_EPI0S3);

GPIOPinConfigure(GPIO_PC7_EPI0S4);

GPIOPinConfigure(GPIO_PC6_EPI0S5);

GPIOPinConfigure(GPIO_PC5_EPI0S6);

GPIOPinConfigure(GPIO_PC4_EPI0S7);

GPIOPinConfigure(GPIO_PA6_EPI0S8);

GPIOPinConfigure(GPIO_PA7_EPI0S9);

GPIOPinConfigure(GPIO_PG1_EPI0S10);

GPIOPinConfigure(GPIO_PG0_EPI0S11);

GPIOPinConfigure(GPIO_PM3_EPI0S12);

GPIOPinConfigure(GPIO_PM2_EPI0S13);

GPIOPinConfigure(GPIO_PM1_EPI0S14);

GPIOPinConfigure(GPIO_PM0_EPI0S15);

GPIOPinConfigure(GPIO_PL0_EPI0S16);

GPIOPinConfigure(GPIO_PL1_EPI0S17);

GPIOPinConfigure(GPIO_PL2_EPI0S18);

GPIOPinConfigure(GPIO_PL3_EPI0S19);

GPIOPinConfigure(GPIO_PQ0_EPI0S20);

GPIOPinConfigure(GPIO_PQ1_EPI0S21);

GPIOPinConfigure(GPIO_PQ2_EPI0S22);

GPIOPinConfigure(GPIO_PQ3_EPI0S23);

// Commented out lines represent GPIO used elsewhere

//GPIOPinConfigure(GPIO_PK7_EPI0S24);

//GPIOPinConfigure(GPIO_PK6_EPI0S25);

GPIOPinConfigure(GPIO_PL4_EPI0S26);

GPIOPinConfigure(GPIO_PB2_EPI0S27);

GPIOPinConfigure(GPIO_PB3_EPI0S28);

GPIOPinConfigure(GPIO_PN2_EPI0S29);

//GPIOPinConfigure(GPIO_PN3_EPI0S30);

GPIOPinConfigure(GPIO_PK5_EPI0S31);

GPIOPinConfigure(GPIO_PK4_EPI0S32);

GPIOPinConfigure(GPIO_PL5_EPI0S33);

GPIOPinConfigure(GPIO_PN4_EPI0S34);

GPIOPinConfigure(GPIO_PN5_EPI0S35);

// Set GPIO to EPI

GPIOPinTypeEPI(GPIO_PORTA_BASE, EPI_PORTA_PINS);

GPIOPinTypeEPI(GPIO_PORTB_BASE, EPI_PORTB_PINS);

GPIOPinTypeEPI(GPIO_PORTC_BASE, EPI_PORTC_PINS);

GPIOPinTypeEPI(GPIO_PORTG_BASE, EPI_PORTG_PINS);

GPIOPinTypeEPI(GPIO_PORTK_BASE, EPI_PORTK_PINS);

GPIOPinTypeEPI(GPIO_PORTL_BASE, EPI_PORTL_PINS);

GPIOPinTypeEPI(GPIO_PORTM_BASE, EPI_PORTM_PINS);

GPIOPinTypeEPI(GPIO_PORTN_BASE, EPI_PORTN_PINS);

GPIOPinTypeEPI(GPIO_PORTQ_BASE, EPI_PORTQ_PINS);

//

// Set the EPI divider.

//

EPIDividerSet(EPI0_BASE, 1);

//

// Select GPIO

//

EPIModeSet(EPI0_BASE, EPI_MODE_GENERAL);

//

// Activate External CLK on EPI0s31, Set data to 24 bits EPI0s0 to EPI0S23

//

EPIConfigGPModeSet(EPI0_BASE,ulEPIConfig,0,0);

//

// Set the address map.

//

EPIAddressMapSet(EPI0_BASE, EPI_ADDR_RAM_SIZE_256MB | EPI_ADDR_RAM_BASE_6);

//

// Start the EPI Interface

//

EPINonBlockingReadConfigure(EPI0_BASE, 0, EPI_NBCONFIG_SIZE_32, 0);

EPINonBlockingReadStart(EPI0_BASE,0,1);

}

/////////////////////////////////////////////////

// Draw the GUI on the Screen

//////////////////////////////////////////////

void GUI()

{

myScreen.setOrientation(1);

myScreen.setFontSize(0);

myScreen.gText(4, 4, "V/D " + String(1) + ", Time/D: " + String(1)+ ",R/F: " + String(1) , colour_white);

for(int x = 1; x < 320; x++){

if(x%20 == 0){

if(x == 20*8){

//Long Vertical Axis

for(int i = -120; i < 120; i++){

myScreen.point(x, 120 + i, colour_white);

//myScreen.point(x, 240 + i, colour_white);

if(i%20 == 0 && i != -120){

// Lines on Vertical Axis

for(int y = -6; y < 6; y++){

myScreen.point(x+y, 120 + i, colour_white);

//myScreen.point(x+y, 240 + i, colour_white);

}

}

}

}else{

// Ticks on Horizontal Axis

for(int i = -5; i < 5; i++){

myScreen.point(x, 120 + i, colour_white);

//myScreen.point(x, 240 + i, colour_white);

}

}

}

myScreen.point(x, 120, colour_white);

//myScreen.point(x, 240, colour_white);

}

}

//////////////////////////////////////////

// GUI UPdate

// - Updates the GUI based on the input

////////////////////////////////////////

void GUI_update(uint8_t v_div,uint8_t t_div, uint8_t risefall )

{

myScreen.setFontSize(0);

myScreen.gText(4, 4, "V/D " + String(v_div) + ", Time/D: " + String(t_div)+ ",R/F: " + String(risefall) , colour_white);

delay(100);

}

///////////////////////////////////////////////////

// sSets Gain

// The pins in order control - D0, D1, D2, D3, D4, D5, D6 of the PGA. This sets up these pins to the inputed state.

///////////////////////////////////////////////////

void setGainData(int d6, int d5, int d4, int d3, int d2, int d1, int d0){

if(d0 == 1){

digitalWrite(51, HIGH);

}else{

digitalWrite(51, LOW);

}

if(d1 == 1){

digitalWrite(53, HIGH);

}else{

digitalWrite(53, LOW);

}

if(d2 == 1){

digitalWrite(58, HIGH);

}else{

digitalWrite(58, LOW);

}

if(d3 == 1){

digitalWrite(74, HIGH);

}else{

digitalWrite(74, LOW);

}

if(d4 == 1){

digitalWrite(73, HIGH);

}else{

digitalWrite(73, LOW);

}

if(d5 == 1){

digitalWrite(72, HIGH);

}else{

digitalWrite(72, LOW);

}

if(d6 == 1){

digitalWrite(71, HIGH);

}else{

digitalWrite(71, LOW);

}

}

uint16_t size = myScreen.screenSizeX();

int i = 0,x = 0;

uint32_t data = 0;

uint32_t y = 0,z = 0,fill = 0;

unsigned long int timer_value;

volatile int buffer_count = 0;

int triggered = 0;

int temp_test = 0;

double gain = 4;

double old_gain = 4;

int wait = 100;

signed int ya,yb,ya_o,yb_o;

const int TimePin = PUSH1;

const int VoltagePin = PUSH2;

const int TrigPin = 12;

int volState = 1;

int timeState = 1;

///////////////////////////////////////////////

// Initialization Code

/////////////////////////////////////////////

void setup()

{

// Setup PGA Control

setupGain();

setGainData(1,1,1,1,1,1,1);

pinMode(VoltagePin, INPUT_PULLUP);

pinMode(TimePin, INPUT_PULLUP);

attachInterrupt(VoltagePin, voldiv, RISING);

attachInterrupt(TimePin, timediv, RISING);

pinMode(12, INPUT);

setupEPI();

// Start LCD Screen

myScreen.begin();

myScreen.setFontSize(myScreen.fontMax());

//while(1){

// Draw GUI

GUI();

//}

// Fill the old and new buffers

for(x = 0; x <= 319; x+=1){

buffer_a[x] = 0;

old_buffer_a[x] = 0;

buffer_b[x] = 0;

old_buffer_b[x] = 0;

}

i = 0;

buffer_count = 0;

TimerSetup();

attachInterrupt(TrigPin, trigger, RISING);

}

// Loop Code

void loop()

{

//myScreen.gText(40, 40, String(int_sample&0x0000001F));

//

// Software Trigger

// - Waits until a value is read on EPI, once it finds the correct value it starts the timer interrupt to sample the EPI

//if(data_addr[0] != 0 && triggered == 0){

// triggered = 1;

// TimerIntEnable(TIMER1_BASE, TIMER_TIMA_TIMEOUT);

//}

//

// If the Scope was triggered and the buffer of samples was filled

//

if(triggered == 1){

interrupts();

if( buffer_count == 320 ){

// Disable the Time Interrupt

TimerIntDisable(TIMER1_BASE, TIMER_TIMA_TIMEOUT);

noInterrupts();

// DRAW SIGNAL

for(x = 0; x <= 320; x+=1){

ya = ((buffer_a[x]-512+115)/gain+120);

yb = ((buffer_b[x]-512+115)/gain+120);

if(buffer_a[x] != 10 && x % 20 != 0 && ya % 20 != 0){

myScreen.point(x, ya, colour_red);

}

if(buffer_b[x] != 10 && x % 20 != 0 && yb % 20 != 0){

myScreen.point(x, yb, colour_blue);

}

}

// ERASE OLD SIGNAL

for( x = 0; x < 320; x +=1){

ya_o = ((old_buffer_a[x]-512+115)/old_gain+120);

yb_o = ((old_buffer_b[x]-512+115)/old_gain+120);

if(x % 20 != 0 && ya_o % 20 != 0 && old_buffer_a[x] != 10 && buffer_a[x] != old_buffer_a[x]){

myScreen.point(x, ya_o, colour_black);

}

if(x % 20 != 0 && yb_o % 20 != 0 && old_buffer_b[x] != 10 && buffer_b[x] != old_buffer_b[x]){

myScreen.point(x, yb_o, colour_black);

}

old_buffer_a[x] = buffer_a[x];

old_buffer_b[x] = buffer_b[x];

}

//GUI();

myScreen.gText(20, 20, "A: " + String(buffer_a[x]-100));

myScreen.gText(70, 20, "B: " + String(buffer_b[x]-100));

delay(10);

buffer_count = 0;

triggered = 0;

old_gain = gain;

// Start Intrrupts again

interrupts();

TimerLoadSet(TIMER1_BASE,TIMER_A, wait);

}

}

}

// When the voltage per deviation button is pressed this function changes the gain to make displayed signal larger or smaller

void voldiv()

{

volState++;

if(volState == 3){

volState = 0;

}

if(volState == 0){

gain = 8;

}

if(volState == 1){

gain = 4;

}

if(volState == 2){

gain = 2;

}

GUI_update(volState,timeState, 1);

}

// When the time per deviation button is pressed this function changes the time beween samples to change how much of a signal is measured

void timediv()

{

timeState++;

if(timeState == 3){

timeState = 0;

}

if(timeState == 0){

wait = 150;

}

if(timeState == 1){

wait = 300;

}

if(timeState == 2){

wait = 600;

}

GUI_update(volState,timeState, 1);

}

// When trigger is seen this function is called and starts collecting samples

void trigger()

{

triggered = 1;

interrupts();

TimerIntEnable(TIMER1_BASE, TIMER_TIMA_TIMEOUT);

}

//

// Timer Interrupt Initalization

//

void TimerSetup(){

SysCtlPeripheralEnable(SYSCTL_PERIPH_TIMER1);

TimerConfigure(TIMER1_BASE, TIMER_CFG_PERIODIC);

TimerIntRegister(TIMER1_BASE, TIMER_A, Timer1IntHandler);

TimerEnable(TIMER1_BASE, TIMER_A);

TimerLoadSet(TIMER1_BASE,TIMER_A,150);

IntEnable(INT_TIMER1A);

}

//

// Timer Interrupt Handler

//

void Timer1IntHandler(void) {

// Clear the timer interrupt

TimerIntClear(TIMER1_BASE, TIMER_TIMA_TIMEOUT);

// If the buffer is not filled and the scope is triggered

if( buffer_count < 320 && triggered == 1){

// Get sample from EPI

sample = data_addr[0];

// Store First Sample

buffer_a[buffer_count] = sample&0x00000003FF;

// Store Second Sample

buffer_b[buffer_count] = (sample>>10)&0x000003FF;

// Count Number of Samples

buffer_count++;

}

}

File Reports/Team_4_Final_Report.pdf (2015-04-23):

1 | P a g e

To: Trey German, Advisors

From: Team 4, Eric Taylor and Raymond Montgomery

Date: 4/20/2015

Subject: Final Report

## Executive Summary

This project's objective was to design an oscilloscope BoosterPack (a hardware extension of a LaunchPad) that is compatible with TI LaunchPads (a programmable micro controller and its peripherals) that is a low cost alternative to the typical desktop oscilloscope. This project was open source so anyone can learn from the hardware and software design and be able to expand upon them. The final product must be able to function as a reliable oscilloscope at an affordable cost to both hobbyists and students. As a low end design, the oscilloscope BoosterPack needs to push its cost down as much as possible while having the features of a typical oscilloscope. The main goal was to create a BoosterPack that has two measurement channels that can take a +/- 15V signal and has a bandwidth of 7MHz for under $50. Future work on a similar project should look into being able to take the full capabilities of the ADC and adjusting the front end so it can be attached to a multitude of probes.

## 1. Introduction and Project Overview

Our client Trey German from Texas Instruments (TI) wants a BoosterPack that can function as a low cost oscilloscope for TI's series of LaunchPads. This project would be available to both hobbyists and professionals so they can easily buy and attach this BoosterPack to a LaunchPad and have a low cost oscilloscope. This BoosterPack is compatible with the Tiva C Connected LaunchPad so TI can expand its market for LaunchPad, BoosterPack, and Energia (TI’s open source C++ programming language) products by utilizing resources made by TI. With the successful completion of the oscilloscope BoosterPack there will be a lower cost alternative for the current oscilloscopes that are available on the market. The client would like the designs and code to be open source, the coding to be done in Energia, a user’s manual, a prototype of the design, and the code and designs used to create the prototype. We were able to create an oscilloscope BoosterPack that was able to take inputs from two channels and trigger off one. The signals can range from -1.5V to 1.5V and has a bandwidth of 200k. These shortcomings can be solved in software with some additional hardware as you will read later.

## Contents

## 2. Accomplishments

The project was to create an oscilloscope BoosterPack for TI’s Launchpad series which had the following features: two measurement channels, hardware triggering, user control, 6.5 MHz bandwidth, and +/ 15V input swing for all under $50. The reasoning behind the selection of these features can be seen below. In our final product we were able to accomplish most of what was needed but not all. The BoosterPack did have two working channels and a hardware trigger for under $50, however the software could not sample fast enough to get the 6.5 MHz bandwidth and adjustments are needed on the front end to get a full +/- 15 V input swing. The final board we made had a 200 kHz bandwidth and +/- 1.5V input swing.

### 2.1 Description of the Primary Stakeholders and Features

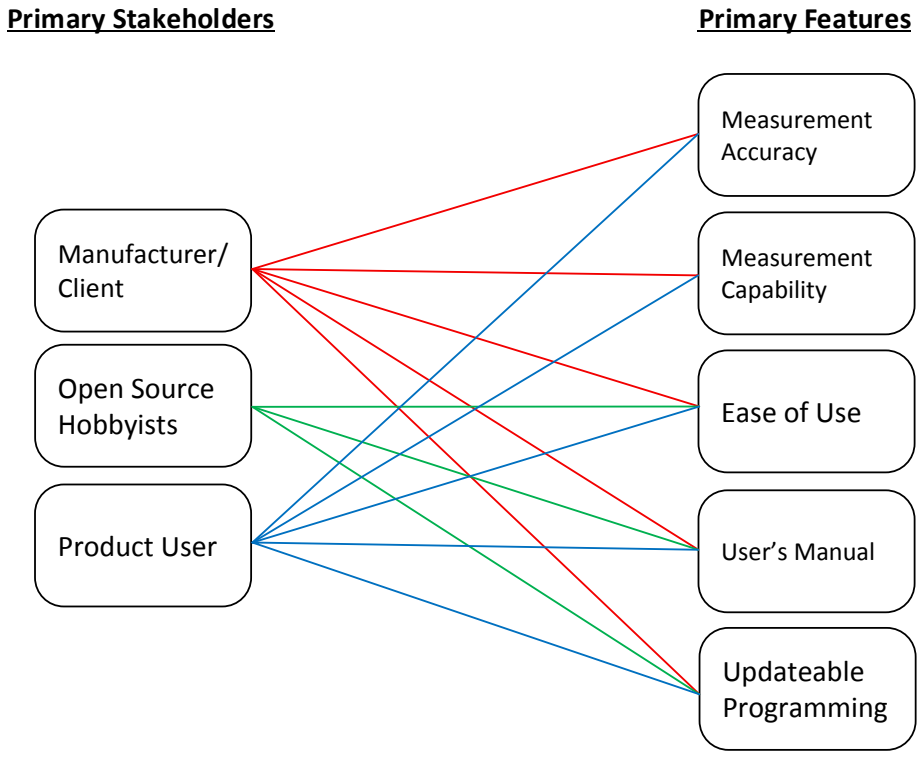
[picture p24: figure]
Manufacturer/ Client; Open Source; Hobbyists Product User; Measurement; Programming; Measurement Capability; Primary Stakeholders; Primary Features

# Accuracy Ease of Use User’s Manual Updateable

Figure 1. Primary Stakeholders and Features

The final product which consists of our physical circuit, the code that runs it, and the open source material all of which are determined by the primary stakeholders and features of our system. The client, TI, provided this project submission and therefore cares about all the deliverables they requested. Anyone who uses the oscilloscope BoosterPack wants a functional final product and would want to reference the open source material for debugging errors and exploring the design of the product. Those who do own the product (like hobbyists and other recreational researchers) can still view the open source materials for studying circuit and code designs. The remaining features describe the actual function of the oscilloscope BoosterPack. ‘Measurement Accuracy’ and ‘Measurement Capability’ are distinct and necessary features for the final product. The accuracy describes the how well the oscilloscope BoosterPack’s measurements are to the actual signal being measured, while capability is a necessary step in determining signal accuracy because we need confirm that the data displayed on the oscilloscope is measurement data. Since the program on the circuit’s microcontroller can be changed, the user can see how making changes to the program can affect the operation of the oscilloscope and other programs can be loaded onto the LaunchPad so it can be used for different projects. As the project becomes easier to use, the user enjoys using the oscilloscope BoosterPack more which is why ease of use is a primary feature.

### 2.2 Description of the Solution


Figure 2. Domain Diagram

In figure 2 the domain model of the project is presented. In this model the outside actors of the system are identified along with their interactions with the system. The first actor are the probes that are used in conjunction with the system. This directly related to measurement accuracy, ease of use, price limit, and measurement capabilities. The probes are what connects the signal to the circuit and have characteristics like input impedance and signal attenuation. These can effect what type of signal that could be measured and how accurate the system can be. The probes are also a separate component to reduce cost of the final package, and the user can use ones to their specification. For the final board design any BNC probe could be attached to measure signals. However when the 10x setting is used the signal does not go through. Further research is needed to figure out why this happens.

The next outside actor is the user which adjusts the settings, assembles/updates, and in general uses the scope. This directly relates to the ease of use, instruction manual, measurement capabilities, and price limit. The user needs to be able to operate the scope with ease, and should have a similar interface to other scopes on the market. This coincides with the user manual which explains the use of the scope to the user. Finally the user wants to be able to buy the product at a reasonable price given the performance the scope has. This was satisfied using buttons that came attached to the LaunchPad and a potentiometer attached to the BoosterPack. These controls allowed the user to adjust time and voltage per deviation, and also adjust the trigger level. Using controls that came with the LaunchPad also reduced the total cost of the board.

The next outside actors are outlet which directly effects power consumption, shipping which involves how the product is packaged, and the signal which related to accuracy and capability. The outlet determines how much power the scope can use. For power the final board can be powered by any micro usb source including portable battery packs. The shipping of the product relates the manufacturability and how the product is packaged. This was accounted for in the hardware design of the board. Finally the signal shape, size, and characteristics need to be known so the scope can be made to measure the variety of signals that it needs.


Figure 3. Logical Architecture

In figure 3 we see the logical architecture of the system which describes how the scope will respond to the outside actors and shows how the system will function in general. Following the flow of the signal first comes the analog front end which accepts the signal from the scopes and proceeds to attenuate/amplify the signal, apply the proper common mode voltage, and make it differential. The signal is also put through a filter to reduce high frequency noise. The signal then proceeds to the ADC where it is sampled and then read into the memory of the microcontroller. The microcontroller the uses these samples and based on the user input displays the signal on a LCD screen.

The front end involves many parts, first of which is the THS4121 which does the single to differential conversion. This part was a cheap general part that is able to handle +/- 1.5V swings which was appropriate because we planned 10x probes working with the board which they did not. With 10x probes the +/- 1.5V swing would be enough for a +/- 15V input. This part also had the necessary bandwidth to handle 10 MHz signals.

The next part used was the programmable gain amplifier, LMH 6882. This part was first suggested by the client and worked well for our purpose. This amplifier has up to 25dB gain allowing for the measurement of small signals. This part also had two channels which reduced the part count on the board reducing cost.

Next came the sampling system or ADC. The ADC chosen was the ADS5237. This part had a sampling rate of 65 MSPS which allowed the measurement of signals up to 7MHz assuming the industry guideline of having 10 samples per period to have a good measurement on a signal. It also was selected because it had two channels which reduced part count and was relatively cheap compared to other ADCs that were up for consideration. Finally it had 10-bits of resolution which the client stated he wanted in the planning process.

The microcontroller which takes in the samples was satisfied using the Tiva C connected LaunchPad from TI. This board was needed because of the extra pins that were included which were needed to satisfy all of the requirements. This board also had EPI which was needed to receive the 20-bit data signal for both channels at appropriate speeds.

Other blocks include the triggering circuit which takes in the filtered and unfiltered signal and tells the microcontroller when to start sampling based on a desired trigger level. This was done using cheap general purpose op-amps because of their low cost, and had satisfactory bandwidth for our features. The power circuit takes in the power from the outlet or USB and provides the microcontroller and the circuit with power. The power circuit was on the LaunchPad itself and no further circuitry was needed. The package block includes how it has to be manufactured to be able to interact with the Launchpad. This will be done by following BoosterPack templates and specifications. Finally the mechanical control which includes buttons which are on the Launchpad and a potentiometer which is on the BoosterPack.

Finally the display requirement was satisfied by an external BoosterPack made by a third party. This allowed us to focus on other features while satisfying a requirement at low cost. A simple 2.2” LCD controlled by SPI was used because of its low cost and simplicity to control.

This solution is able to deal with all of the major features which includes measurement accuracy, ease of use, measurement capabilities, updateable programming, and user manual. The measurement accuracy and capabilities are determined by the front end and ADC. Ease of use is taken care of by the mechanical control, display, and probes. However it couldn’t fully handle the features because the software wasn’t able to take in samples fast enough. The hardware could handle this requirement but software could not. Other than this detail the hardware selected was able to satisfy all of the requirements

### 2.3 Data and Verification of Requirements

Some requirements that relate to the primary stakeholder features are shown below.

### Black Box

Interaction | ID | Actors | Requirement
Inputted Signal | BBDI-1 | Probes, Signal | The inputted signal must be between +15V and – 15V
Inputted Signal | BBDI-2 | Probes, Signal | The inputted signal must be below 7 MHz to be properly sampled and measured.
Adjust Settings | BBAS-2 | USER | The user must be able to change the time scale of both channels.
Adjust Settings | BBAS-3 | USER | The user must be able to change the voltage scale of both channels.

### White Box

Interaction | Req-ID | Blocks | Requirement
Measuring Signals | WBMS-2 | Triggering Circuit | The signal input to the Triggering Circuit should be scaled down to a range of 0V to 2V.
Measuring Signals | WBMS-4 | Triggering Circuit | The output signal should stay within the range of 0V to 5V.
Measuring Signals | WBMS-6 | Triggering Circuit | The potentiometer should be controlled by the user with an external, mechanical interface.
Measuring Signals | WBMS-7 | Triggering Circuit | The output signal should range from 0V to 3.5V (due to op-amp saturation).

Most of these requirements deal with ease of use and how the user is able to interact with the scope. The measurement accuracy and capabilities are also touched upon in the requirements. The block box requirements directly relate to how the user can adjust the settings and the measurement capabilities of the scope. These were primarily tested using the analog front end because that is what determines these characteristics. The white box deals with the triggering circuit and how the user is able to adjust the trigger level of the circuit.

### White Box Testing

As said before for the white box requirements we tested the triggering circuit. First to test these requirements we had two input signals are averaged and are compared to a trigger level voltage controlled by a disk potentiometer. Power supplies of -5V and +5V are used. The averaged output voltage, trigger level voltage, and the output voltage of the system (output of comparator) are measured using an oscilloscope. These measurements help prove the ‘linearity’ of the trigger level voltage, the limits of the input range, and the propagation delay. The following diagram was the result.


Figure 1: Highest input voltage. Both input signals have f = 1 kHz and their values range from -1.5V to +1.5V. (Green – Trigger Level, Yellow – Signal, Purple – Output)

The averaged output has an appropriate frequency (f = about 1 kHz) and an appropriate amplitude (about 3Vptp). These results agree with the requirements and expectations of the system. The trigger level voltage is correctly shaping the logical output of the comparator.


Figure 2: Lowest input voltage. Both input signals have f = 1 kHz and their values range from -50mV to +50mV.(Green – Trigger Level, Yellow – Signal, Purple – Output)

The averaged output has an appropriate frequency (f = about 1 kHz) and an appropriate amplitude (about 100mVptp). These results agree with the requirements and expectations of the system. The trigger level voltage is correctly shaping the logical output of the comparator.

Graph for Trigger Level ‘Linearity’:

Pulse Width; Trigger Level Voltage (V); Trigger Level Lineraity

The variation of the pulse width of the logical output of the comparator shows that the trigger level voltage can appropriately be compared with the averaged output signal at all (numerous) values of the trigger level voltage.


Figure 4: The propagation delay of the logical comparator output voltage is shown. (Green – Trigger Level, Yellow – Signal, Purple – Output)

Trigger Level Voltage | Duty Cycle
500mV | 5%
624mV | 15%
890mV | 25%
1.97V | 50%
2.98V | 75%
3.14V | 80%
3.39V | 93%

The propagation delay is shown to be ΔX = 1.2 us. This propagation delay is too high because our oscilloscope should measure signals up to 7 MHz whose period is shorter than the propagation delay which causes a problem with sampling the signal at inappropriate times.


Figure 5: The result of having the maximum input frequency is shown. (Green – Trigger Level, Yellow – Signal, Purple – Output)

The maximum frequency that the system can handle and still maintain desired operation is 150 kHz. This much too low of a frequency (150 kHz << 7 MHz). This low maximum frequency is caused by the slew rate on the comparator amplifier. The limits of the comparator amplifier also affect the propagation delay.

We concluded that the comparator amplifier can be replaced with the amplifier that used to average the input signals. This will improve the propagation delay to an appropriately small value. This will also increase the maximum operation frequency of the system. Our final product included this amplifier and worked as intended.

### Black Box Testing

For the black box testing we wanted to confirm the input requirements to the scope. This includes features like how high frequency of a signal can be inputted to the scope, and how large of a signal. This testing revolved around the front end because that is what takes the input signal and delivers it to the ADC for sampling.

For the setup of this testing the final board was made so a scope probe can take an input signal and there were testing wires soldered to the output of the analog front end right before the ADC. This allows us to see when a certain signal is inputted that the signal gets to the ADC correctly to be sampled. Here we are mostly looking for shape because depending on the settings of the programmable gain amplifier the true amplitude is unknown and is only known to the microcontroller which provide the correct gain factor to the samples. For the sake of this testing the lowest settings of gain were used for the programmable gain amplifier.

To start testing the functionality was confirmed with a 50mV input which is reality simulates a .5 V input because of the 10x probes (probes used were set at 1X). At 50 mV a sine wave was put through at 1kHz, 100kHz, 1MHz, and 10 MHz in addition to a square wave at 1MHz and a ramp wave at 200kHz. Again here we want to confirm the correct shape going into the ADC.

These test address the requirements of BBDI-1 and BBDI-2 which both describe characteristics of the input signal.

Here are the results of the first round of testing. (Yellow – Input, Green – Output)


Figure 1. 50 mV Sine at 1kHz


Figure 2. 50mV sine at 100kHz


Figure 3. 50mV sine at 1Mhz

Figure 4. 50mV sine at 10MHz


Figure 5. Square Wave at 1MHz

Figure 6. Ramp Wave at 200kHz

From these plots we can conclude that the front end functions properly at small signals and at high enough frequencies. For the next set of testing the limits of the requirements were tested to see if there was any degradation of the signal at the limits of the PGA.

The second round of testing includes an input signal of 1.4V simulating a 14V input on 10x probes. 1.5V was tried but the signals saturated failing the 15V goal. However the behavior still should be tested at the max input level. The same tests were performed as before. The only change was the input level of the signal.

Here are the results (Yellow – Input, Green – Output):


Figure 7. 1.4V Sine at 100KHz


Figure 8. 1.4V Sine wave at 1MHz

Figure 9. 1.4V Sine wave at 10MHz


Figure 10.1.4V Square wave at 1MHz

Figure 11. 1.4V Ramp at 200kHz

Conclusions:

For the first round of testing all the signals were able to be seen through the PGA with minimal distortion. When the frequencies were increased to 10MHz the tests were approaching the limits of the signal generator which can be seen in the input signal causing distortion on the output signal. This can be seen in the yellow input signal on the graphs. These tests also show the low pass filter has to be looked at to get rid of some of the noise on the input signal.

For the second round of testing where the amplitude was increased the signals became much clearer and more defined. In general a lot better results were seen in terms of the shape of the original signal. This shows us at smaller signals the gain settings may have to be increased to get the optimal shape of the output signal.

Overall the requirements were not met perfectly, but with fixes to the low pass filter with a 10 MHz bandwidth, using the correct gain settings on the PGA controlled by software, and putting a small 1/10th voltage divider to allow the full +/- 15V range, the front this system can achieve its requirements. These were implemented on the final board. However since the 10x probes didn’t work as intended the full range could not be used. This could be fixed by adding a smaller voltage divider on the front end to reduce the signal more coming in essentially doing the attenuation a 10x probe would do.

## 3. Project Plan and Timeline

Formulation of the Design Problem; Research Oscilloscopes and Start Defining Specifications; Start Making System Documentation; Outline System Documentation; Find Relative Open Source Information and Kits; Analog Front End Research/Design; EPI Research and Design; Display Research and Design; Application Software Research and Design; PCB Design; Project Documentation; Analog Front End Research and Design; ADC Research and Design; Trigger Level Research and Design

### Fall Quarter

Figure 1. This section of the timeline shows the initial plans and the actual progress made during the first 10 weeks of work on our project (50% of our allotted time to work on the project).

The original timeline, shown in black at the bottom, has four major categories. Weeks 1 to 3 initialize the project team and help define the goals of the project. The rest of the time consists of documentation, hardware, and software progress. Documentation includes all reports required of the project for the ECE460 and ECE461 Senior Design classes. Several PCBs needed to be designed to efficiently test the hardware subsystems of the oscilloscope BoosterPack. Then these subsystems are all connected on a final board for testing the final, complete hardware design. The code for the software is all done with Energia, a TI software application. Hardware is the most vital part of the project because all project goals depend on the hardware. Software needs hardware as an interface and therefore cannot be fully tested without it. Data used in documentation is only collected from hardware.

PCB Design; Assemble System to Test Prototype; Revise Design; Product Testing; Revise Documentation; Ship to Client; Winter Quarter; Spring Quarter; Extension; Project Done; Project Documentation; Subsystem PCB Design/ Subsystem Design Testing/ Subsystem Design Revision; Application Software Research and Design; Final Board Design/ Final Board Testing/ Final Board Revision

Figure 2. This section of the timeline shows the initial plans and the actual progress made during the last 10 weeks of work on our project (50% of our allotted time to work on the project) but also shows our progress during our 3 week extension for our project.

Our actual progress, shown in blue at the top, definitely has differences from the original. Our client explained some helpful block diagrams during our client drop-in and this helped us to become ready to start designing hardware and software earlier. Project documentation took more time out of the quarter than expected and it felt like a distraction from developing software and hardware, increasing the span of time spent on research and design. PCB design involved a large amount of debugging caused by numerous sources (soldering errors, PCB file design errors) and pushed back the design for the final board/product. While burdened with hardware difficulties, we made minimal progress on the software. There are deviations from our original plan that cannot be seen in the timeline. There was some confusion about the definition of our project in the first few weeks which delayed our preliminary research. Originally group of 3 people, we lost a group member as soon as Week 11 started. This made it even more difficult to put in enough hours to match the development of 4 people when we are only 2 people.

Certain deviations from our original timeline were easy to see but others could be undetected because they lack due dates or checkpoints to remind us of where our progress should be. To improve detection of deviations, there could be an assigned person to constantly monitor the progress of all assignments or every person can report their shortcomings or difficulties as soon as they arise. The best way to prepare for unknown problems is to welcome every opportunity of the problem. In our case, one person could have made a PCB as soon as possible to discover what problems can arise with PCB design. Then the impact of the problems with one PCB would only be a fraction of the problems with multiple PCBs, therefore saving time by not solving the same problems multiple times.

## 4. Recommendations

Our project has fallen short of its expectations and its goals. The hardware is capable of handling the range of input signals (frequencies up to 7MHz) but the software can’t handle samples fast enough. A micro DMA method in software would help to handle samples faster and enables the oscilloscope BoosterPack to appropriately handle and display the higher frequency signals by writing the samples directly to memory when they are received. The software also doesn’t dynamically change the gain of the PGA to amplify smaller signals. However the control signals to do so are in hardware. More software would have to be added to allow the oscilloscope BoosterPack to measure the range of signals that we designed for. Finally adding a selectable attenuator to the front end would allow the hardware to accept larger signals. These recommendations would help the project to better meet the stakeholder features for Measurement Accuracy. Overall the core functionality works, meeting the Measurement Capability, Open Source Material, Ease of Use, and Updateable Programming features, but adding more software would allow the board achieve all its goals, and adding some hardware could help the project to meet these goals.

## 5. Going Further

### 5.1 Standards

Many standards went into our project. The BoosterPack interface design is standard because every BoosterPack and LaunchPad need to have certain dimensions and locations for pin headers so the BoosterPacks can be stacked on top of the LaunchPad. Our project is taking advantage of this to not only attach the oscilloscope hardware to the LaunchPad, but also the display on top of our BoosterPack.

The power coming into the BoosterPack is supplied through a standard 5V at 1A USB power supply converter on the LaunchPad. This powers all of the hardware on the board including the display.

Signals are measured through standard mechanical BNC connectors and 10x attenuation capable probes.

The display used for the BoosterPack has a SPI display driver and the code for the LaunchPad is configured specifically for this type of display driver.

If the product reaches the end of its life then the materials used to fabricate and populate the PCB are ROHS (Restriction of Hazardous Substances Directive) certified so the product can be disposed in an environmentally friendly manner.

### 5.2 Manufacturability/Safety

Many features of our project took into consideration the manufacturability of the product. All ICs used to populate the board are TI brand ICs and all parts can be bought from one supplier, DigiKey, which makes it easy and cost efficient to supply components. The types of ICs and the different values of resistors, capacitors, and inductors were minimized to have less variation in the components therefore making it easier to supply them.

There are however areas of improvement in terms of manufacturability of the project. The BNC connectors have electrical connections and physical connections to the PCB board. The pins are connected to the circuit but there are stubs on the bottom of the connectors that increase the stability of the mount on the PCB. This alone doesn’t provide enough support and the connectors can be more secure by placing an adhesive between the bottom of the connectors and the mask on the PCB. Test points should be added for the AFE and other areas to help with debugging the hardware. Finally the PGA has a heat pad on the bottom which should be soldered with IR to reduce the temperature of the chip.

There are also some safety concerns. There are places where we have soldered components so each solder point is an exposed electrical connection. After the PCB is populated, a mask can be placed over the board to cover the points.

### 5.3 System Failure Mode Analysis

If the system is used inappropriately the product could fail and cause permanent damage to itself. The PGA on the BoosterPack could overheat if too high power of a signal is inputted or the scope is left on for an elongated period of time. This is because the bottom thermal pad of the PGA could not be soldered by us, however in manufacturing would be able to be soldered making this problem moot\. This could burn the chip and the component would need to be replaced. A user error could measure signals outside the specified amplitude range which could burn components by supplying too much power in terms of the input signal. This error shouldn’t be happen if the user the BoosterPack under the specified conditions. This error would be hard to detect and debug because it depends on which component burns first. Another user error could be an incorrect orientation of the BoosterPack on the LaunchPad while power is on (plugged in). This might occur somewhat frequently if the user is not paying attention to the arrangement of the pin headers when the BoosterPack and LaunchPad are connected. An incorrect connection due to this error could cause a short and burn a component. This error would be hard to detect and debug because it also depends on which component burns first.

### 5.4 Societal Impact

The oscilloscope BoosterPack should make the reliable function of an oscilloscope more available to the general public. Mainly students or hobbyists doing electrical work would benefit from having this product on the market because this gives a low cost solution to measuring signals. With the open source material and the function of our product, there will be an increase in the exploration of the science behind electronics. People might be interested in engineering at an earlier age because of the affordable price and the open source information that can aid in teaching the user. This also opens up the possibility of a portable scope that every student can have to do in class or out of class labs with.

### 5.5 Economic Impact

There will be an increase in the number of people that have access to equipment that has a reliable oscilloscope function. With lower cost oscilloscopes in the market, there will be less purchases for higher end oscilloscopes. The cost of higher end oscilloscopes might fall.

## 5.6 Environmental Impact

The BoosterPack is ROHS certified and can be disposed and recycled properly. The owner should take the product to an appropriate electronics recycler. A failure to recycle or dispose properly could harm the environment. Some parts will never break down on the environment and other may decompose, releasing chemicals that could harm the environment.

## 6. Bibliography

Annotated List of Research Memos

[1] Yaohui Wang, Research of Analog Front End Design. October 7, 2014.

Description of the purpose and operation of an analog front end and looked into characteristics our group should look at when making our analog front end.

[2] Eric Taylor, Hold-Off Triggering, September 28, 2014.

A description of what hold off triggering is and how it works. This provided understanding of an oscilloscope feature that could be put into the scope at a later date.

[3] Raymond Montgomery, Oscilloscope Triggering. October 15, 2014.

This provided research into how our project will handle the triggering in hardware and gave understanding into which parts we should use and the general circuit subsystem that had to be made. This deals more with triggering hardware whereas the previous memo is software triggering features.

Annotated Biblliography

[1] I. King , High Performance Analog Front Ends, Analog Edge, Vol. IV Issue 1.

This source was used when the group didn’t have a good understanding of the purpose of an analog front end, and what characteristics of one made it a high performing one. This provided characteristics for the analog front end that our group could shoot for and design around.

[2] Microchip Technology Inc. Non-Inverting Summing Amps August 25, 2014. [Online]

This webpage explains the operation of amplifier circuits that sum signals together. This is useful in the triggering circuit to sum together the filtered and unfiltered signals.

[3] Circuits Today. Voltage Comparator. November 25, 2011. [Online]

This article was used to explain the user of voltage comparator circuits used in the triggering subsystem of our design.

[4] EEVBlog. Oscilliscope Trigger Holdoff Tutorial. March 29, 2011. #159 [Online]

This video provided understanding of holdoff triggering and how we could add it as a feature ein our final scope.

[5] Texas Instruments. Oscilloscope Solution. [Online]

This is a compilation of resources by Texas Instruments that describes solutions and systems needed to make an oscilloscope. This was useful to learn all the systems we needed for our final project.

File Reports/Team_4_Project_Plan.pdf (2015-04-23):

To: Mark Yoder, TI
From: Eric Taylor
Raymond Montgomery
Yaohui Wang
Date: 10/5/2014
Subject: Project Plan

### Executive Summary

The purpose of this project is to provide both hobbyists and professionals with an oscilloscope that they can use for their day to day projects. Current options are fairly expensive in the above $100 range and can be too expensive for the common hobbyist so we want to provide a cheaper solution. To make this scope we want to make
a BoosterPak for a common TI LaunchPad so the user would just have to buy the BoosterPak and attach it to the LaunchPad to have a high performing scope.
The BoosterPak we are designing would consist of a high performance Analog to Digital Converter that can sample at high rates to measure signals up to 25MHz, and also include a black/white colored screen. The user then can control the two channels on the oscilloscope with mechanical buttons and knobs attached on the LaunchPad. Overall the results of this project could be useful to a wide scope of engineers and provide a priced under $50 and reliable measuring tool that they can use on their projects.

### Project Workflow (1st Quarter)


The thought process going into making the first quarter project flow was to get all necessary research and understanding to start making our first prototype going into the second quarter. This is so we can hit the second quarter running in terms of having a working device.

The initial research goes into how the scope parts will fit together. What design considerations we need to keep in mind and start creating specifications for each sub system. Once we have a good understanding of the whole system we break off into each subsystem researching how it works, getting an initial circuit design, and start seeing how the code will have to come together. After that is accomplished we move into designing the PCB for each system to start testing them. It’s almost like a broken up prototype.

### Project Workflow (2nd Quarter)


The purpose of the second quarter is to get the final prototype in ready to ship conditions. With the work coming from the first quarter we have a good idea of the system level design of the scope and started making the first prototype board in the PCB design block. Once this initial design is done we want to get the system put together and the software to be able to communicate with each part if the system.

Once we get our first prototype we start going through design cycles in both hardware and software to get to a final version. While this is happening we will probably revising our documentation and user’s manual. Once an acceptable prototype is made we want to create a final system and start testing. At this point hardware should be solidified and at this point only fixing software.

Once all testing is done we will polish documentation and the user’s manual and ship it off to the client.

### Major Milestones

Milestone | Description
The End of ECE 460 | During this quarter we want to get a complete understanding of the system and its parts. By the end of the term we want working hardware to demonstrate that this project can work. We want
- A working version of the Analog Front End
- A working version of the Triggering Circuit
- A working Display interacting with the microcontroller
- A working ADC interfacing with the microcontroller
| If we have all of these working parts we can start the system integration at the beginning of ECE 461. This is sort of our first prototype but it is split up into sections.
| By working we also mean that they do the job. There may be room for improvement but should be working enough to demonstrate that each component will work and is ready to be implemented in one system.
Midterm of ECE 461 | By the midterm of ECE 461 we want to have complete hardware so the focus can mostly be on software. We want an integrated system of the above parts so it is working. Again there may be room for improvement but we want working hardware to start finalizing the software. The system will include - Working Display - Working Trigger - Working Analog to ADC - Working Controls
End of 1st Complete Version | At the end of the first complete version of software and hardware we want to have a working system where we can start doing final testing. So all of the features listed above should be working. - Math Functions - Triggering - X and Y Scaling
End of 2nd complete Version | The second complete system should have every function working how it is supposed to alongside any additional functions implemented. This should be ready to ship to the client.

### Division of Labor

Team Member: | Division of Labor
Raymond Montgomery | Raymond has taken communication systems and is focusing on analog so he will be working on the Triggering Circuit.
Eric Taylor | Eric will be doing most of the software so he is responsible for the ADC and Display working with the microcontroller. (Connectivity)
YaoHui Wang | YaoHui also works mostly with analog so he will be focusing on the Analog Front End.

### Training Plan

1. In order to complete this project the team needs to
a. Construct an Analog Front End to receive the analog signal and input it to the ADC
b. Have knowledge of the SPI Interface to connect the ADC and Display to the Microcontroller
c. How to process the samples as they come in over the SPI Interface on the microcontroller
d. How to construct a triggering circuit to trigger off a signal
Team Skills
Team Member: | Current Knowledge and Skills
Raymond Montgomery | - Experience with PCB board design - Knowledge of communication systems - Knowledge of signal processing
Eric Taylor | - Knowledge of embedded programming and development - Knowledge of digital signal processing and FPGAs - Some knowledge of Hardware and PCB design
YaoHui Wang | - Knowledge of Hardware Design - Electromagnetic Waves and Field

Team Major Tasks for First Quarter

Team Member: | Tasks | Due Date:
Raymond Montgomery | - Have knowledge of Energia and how it incorporates into our project. - Have initial circuit design of triggering circuit in EAGLE - Initial simulations in OrCAD | End of 5 th Week
| - Create a Working Triggering Circuit on a PCB | End of 10th Week
Eric Taylor | - Have knowledge of Energia and how it incorporates into our project. - Find SPI drivers for Energia and select Display and ADC parts to use. - Buy display and ADC Boosterpacks that I can interface through SPI. | End of 5 th Week
| - Have ADC and Display circuitry on a single PCB that can connect through the Boosterpack Interface. | End of 10th Week
YaoHui Wang | - Have knowledge of Energia and how it incorporates into our project. - Have initial analog front end circuit in EAGLE - Initial simulations in OrCAD | End of 5 th Week
| - Create a Working Analog Front End on a PCB | End of 10th Week

Resources Needed

Resource | Description | Due Date:
Circuit Diagram | We need EAGLE PCB designs of each of the systems by 10th week to start initial prototype design. | Start of 10th Week
PCB Prototype 0v1 | We need the initial prototype to start finishing hardware and getting software started. | Start of 15th Week
PCB Prototype 1v0 | We need to get the first final version of the hardware to start solidifying the software | Start of Week 17
LaunchPads | To start Research into using them for design | End of Week 4
EAGLE | Software used for PCB design. | Start of week 7
Boosterpacks | Boosterpacks to aid in research into system parts | Start of Week 6

### Budget

LaunchPads:; BoosterPacks:; Scope Kits: 11%; Parts: 27%; PCB Fab: 25%; Other: 27%; PRELIMINARY BUDGET ALLOCATION

LaunchPads: | $80
BoosterPacks: | $100
Scope Kits: | $200
Parts (ADC Chips, PGA Chips, Displays): | $500
PCB Fab: | $450
Other (FPGA Dev Kits, Misc. Research Kits): | $500
Total: | $1,830
Budget: | $2,500

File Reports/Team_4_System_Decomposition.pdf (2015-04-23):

To: TI, Senior Project Advisors

From: Team 04

Raymond Montgomery

Eric Taylor

Date 12/10/2014

Subject: System Decomposition 2.0

### Executive Summary

The purpose of this project is to provide both hobbyists and professionals with an oscilloscope that they can use for their day to day projects. Current options are fairly expensive in the above $100 range and can be too expensive for the common hobbyist. To make this scope we want to make a BoosterPack for a common TI LaunchPad so the user would just have to buy the BoosterPack and attach it to the LaunchPad to have a high performing scope. The BoosterPack we are designing would consist of a high performance Analog to Digital Converter that can sample at high rates to measure signals up to 6.5MHz, and also include a colored screen. The user then can control the two channels on the oscilloscope with mechanical buttons and knobs attached on the LaunchPad. Overall, the results of this project could be useful to a wide scope of engineers and provide a price under $50 and a reliable measuring tool that they can use on their projects.

## Analog Front End Decomposition


Figure 1. Functional Diagram

Figure 2. TINA TI Circuit Showing 1 Channel


Figure 3. EAGLE Circuit

For the Analog Front End, there is a BNC probe inputting the single ended signal. The reason we want the probes is to attenuate the signal by 10x and give the input impedance of 1MOhm. This is done because looking into the buffer there is a known high impedance of 1 Mohm and known attenuation.

Next, we have a fully differential amplifier (THS4121). Because the programmable differential amplifier requires two differential inputs, so we use the THS4121 to transfer the single signal to two differential input signals.

Last we have the dual channel differential PGA (LMH6882). The PGA Amplifies small signals so the ADC can measure the signals with proper resolution. This PGA is controlled by the microcontroller through parallel logic telling how much gain the signal need.

Finally there is a low pass filter to get rid of any noise to the ADC with a cutoff frequency of about 10 MHz.

## Triggering Circuit

## Trigger Level Subsystem

Analog Front End; Microcontroller; Averaging Stage; Comparator; Vfiltered; Vunfiltered; Vaverage; User; Vthres; Vout

Figure 4. Trigger System Diagram

## Trigger Level Subsystem

Analog Front End; Microcontroller; Averaging Stage; Comparator; User; Vaverage; Vout

Figure 5. Trigger Implementation Diagram

### TINA TI Diagram


Figure 6. TINA TI diagram of Trigger


Figure 7.Triggering Circuit Diagram

### Summary

After a channel receives a signal. The Analog Front End scales the signal down so the op-amps in the Triggering Circuit can manipulate the input signal within the supply voltages. The user controls the potentiometer with a knob, or a similar control structure. The output of the Triggering Circuit is an array of logical values based on the sampling rate of the microcontroller and if there is one logical high in the array then the waveform is displayed. Logical high is an output of 5V and a logical low is an output of 0V.

## ADC Block Decomposition


Figure 8. System Diagram of ADC Module

Figure 9. Implementation of ADC


Figure 10. Circuit Diagram of ADC Module

### Summary

For our circuit we are going to use the ADS5237 ADC from TI. This chip is a dual channel, 10-bit resolution ADC that can sample at 65 MSPS. This will enable us to measure signals up to 6.5 MHz. This part has a listed use case for test equipment so that also gives reassurance it would be good to use in this case. The chip requires a clock signal from the microcontroller to tell it when to sample, and the data is sent back to the microcontroller over two 10-bit parallel lines. The analog signal coming in comes from the ADC and needs to be a differential signal within 0 to 2 V peak to peak.

Our ADC will not need serial control for now so it is disabled in the schematic for now.

## Microcontroller Decomposition


Figure 11. Microcontroller System Diagram

The microcontroller is the center of the project and will hold all of the software. We are using the Tiva C microcontroller that comes on its generic LaunchPad. The microcontroller is responsible for taking in the sampled data through an EPI bus and storing it into a circular buffer. The trigger then tells the microcontroller when to start displaying data from that circular buffer.

Knowing things such as voltage per division and time per division shown on the screen it will also control the sampling rate through increasing/decreasing the clock frequency to the ADCs. It will also control the amplification through the programmable gain amplifier which is a simple parallel interface.

The microcontroller also takes the user input from mechanical controls such as the push button, rotary encoders, and slide switches, and displays data on a LCD display which it will connect to through the built in SPI drivers.

## Display Decomposition


Figure 12. Display System Diagram

The display we are using only needs a 3.3V supply and a 3 wire SPI to communicate with it.

## Mechanical Input Diagram

Microcontroller User; Mechanical Interface Subsystem; Off; Two State Switch; Push Button; Rotary Encoder; Negative Increment; Positive Increment; No Increment

Figure 13. Input System Diagram

Mechanical Interface Subsystem; Two State Switch; Push Button; Rotary Encoder; User; Microcontroller; Ground; Vout

Figure 14. Mechanical Control Implementation

These mechanical interface inputs allow the user to change menus and sub-menus while also toggling options in these menus. The rotary encoder can be used to navigate through lists, the switch can be used for power to the BoosterPack, and the push button can be used to toggle menu options.

## Power Block

For the power block we needed a way to change 5V coming in from the wall to have supply lines of 5V, 3.3V, and -5V. To get the 5V from the wall we are going to use a barrel transformer coming in with a barrel connector to connect it to the board. Then the 5V coming in will power the LaunchPad, and the LaunchPad will make 3.3V for our system. Then we are going to use a TL7660 to just invert the voltage of the 5V line to get a negative 5V reference for some of the trigger and front end components.


Figure 15. Circuit of getting Negative Reference Voltage

## Validation Matrix

Physical Part/Code Block

Analog Front End

Modify Signal

Microcontroller

Display

Power Circuit

Mechanical Control

Package

Triggering Circuit

ADC

ADS5237 | | | | | | | | | F
OPA2890 | | | | | | | | F
LMH6882 | P | P
THS4121 | P | P
ER-TFTM050-2 | | | | F
612-EG1218 | | | | | | P
COM-09190 | | | | | | P
TIVA C Microcontroller | | | F | | P | | F
TL7660 | | | | | P
Part/Code Block | Block | I/Os | Behaviors Implemented
ADS5237 | ADC | Modified Signal, Sampled Data | This ADC is able to sample a signal at 65 MSPS at 10 bit resolution. This takes care of sampling.
OPA2890 | Triggering Circuit | Filtered , Trigger Signal, Signal | These are general purpose op amps to compare signals to a specified triggering level inputted by the user
LMH6881 | Analog Front End | Signal Modified Signal | This is a programmable gain amplifier that allows us to see really small signals.
THS4121 | Analog Front End | Signal Modified Signal | This is what converts the single ended signal into a differential signal.
TIVA C Microcontroller | Microcontroller | SPI, Mechanical Input, Sampled Input | The TIVA C microcontroller takes in the samples and user input and uses those to manipulate what is displayed.
COM-09190 | Mechanical Control | Mechanical Input | This is a push button switch that allows for user input.
612-EG1218 | Mechanical Control | Mechanical Input | This is a slide switch that allows for user input
ER-TFTM050-2 | Display | SPI, User Output | This is the displays that shows data to the user from the microcontroller.
TL7660 | Power Block | Powers | This is a CMOS voltage converter and is used to change the 5V line to a -5V line for the OP AMPS in the analog front end.

## Decision Matrix

## Solution

Measurement Accuracy
Power Consumption

Ease of Use

User’s Manual
Price Limit

Upgradeable Programming

Signal Measuring
Math Functions

Total

TLC5510 | 3 | 6 | 0 | 0 | 6 | 0 | 4 | 0 | 124
TLC5540 | 3 | 8 | 0 | 0 | 6 | 0 | 7 | 0 | 160
ADS7251 | 7 | 5 | 0 | 0 | 7 | 0 | 2 | 0 | 133
ADS4242 | 8 | 8 | 0 | 0 | 1 | 0 | 9 | 0 | 170
ADS5237 | 6 | 4 | 0 | 0 | 5 | 0 | 9 | 0 | 178
Weight | 6 | 3 | 6 | 5 | 8 | 4 | 10 | 4

The reason we made this selection was because of the focus toward measuring high frequency signals accurately at a relatively low cost. Signal measuring incorporates how many signals the scope can measure and this is measured by seeing how fast the ADC can sample. Both the ADS4242 and ADS5237 have very high sampling rates which allow for measurement in the 10 MHz range, however the ADS5237 is a lot cheaper than its counterpart. Both the ADS4242 and ADS5237 had high resolution (12 and 10 bit respectively) and the ADS4242 did win in this regard. However it wasn’t able to offset the amount it costs. Power consumption is also a consideration, however it is a low one so ADS5237 poor performance in this category was seen as negligible. Overall the ADS5237 was selected because of its high performance while at the same time not being too expensive.

## Black Box Requirements

Interaction | ID | Actors | Requirement
Inputted Signal | BBDI-1 | Probes, Signal | The inputted signal must be between +15V and – 15V
Inputted Signal | BBDI-2 | Probes, Signal | The inputted signal must be below 7 MHz to be properly sampled and measured.
Inputted Signal | BBDI-3 | Probes, Signal | The signal must be able to be attenuated by 10 through the probes. (10x Probes)
Adjust Settings | BBAS-1 | USER | The user must be able to measure each channel with cursors.
Adjust Settings | BBAS-2 | USER | The user must be able to change the time scale of both channels.
Adjust Settings | BBAS-3 | USER | The user must be able to change the voltage scale of both channels.
Adjust Settings | BBAS-4 | USER | The user must be able to control mathematical functions.
Adjust Settings | BBAS-5 | USER | The user must be able to turn on the BoosterPack using a switch.
Assemble | BBA-1 | USER | The use mush only have to attach the BoosterPack to the LaunchPad for it to be functionally operational.
Assemble | BBA-2 | USER | The user must plug in the BoosterPack using a barrel connector for t to have power/
Connect to Circuit | BBCTC-1 | USER. Probes | The user must be able to connect the scope to the circuit through the probes.
Power | BBPI-1 | Outlet | The outlet must provide 5 V and 2 A to the circuit to power its functionality.
Forces | BBPKI-1 | Shipping | The BoosterPack must be tough enough to withstand drops from 5 ft and still be operational.
Forces | BBPIK-2 | Shipping | The BoosterPack must be able to withstand forces from shipping

## White Box Requirements

Interaction | Req-ID | Blocks | Requirement
Measuring Signals | WBMS-1 | Triggering Circuit | The input signal should not exceed a bandwidth (BW) of (max BW determined by the GBW).
Measuring Signals | WBMS-2 | Triggering Circuit | The signal input to the Triggering Circuit should be scaled down to a range of 0V to 2V.
Measuring Signals | WBMS-3 | Triggering Circuit | The potentiometer should be able to use resistance values from 0Ω to 10kΩ.
Measuring Signals | WBMS-4 | Triggering Circuit | The output signal should stay within the range of 0V to 5V.
Measuring Signals | WBMS-5 | Triggering Circuit | The output signal shape should be logical with a low of 0V and a high of 3.5V (due to op-amp saturation).
Measuring Signals | WBMS-6 | Triggering Circuit | The potentiometer should be controlled by the user with an external, mechanical interface.
Measuring Signals | WBMS-7 | Triggering Circuit | The output signal should range from 0V to 3.5V (due to op-amp saturation).
Measuring Signals | WBMS-8 | Triggering Circuit | The output signal should generate a current in the range of -30mA to 30mA.

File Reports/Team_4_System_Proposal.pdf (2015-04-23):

To: TI, Senior Project Advisors From: Team 04
Raymond Montgomery
Eric Taylor

Date 11/12/2014
Subject: System Proposal 2v0

Executive Summary

The purpose of this project is to provide both hobbyists and professionals with an oscilloscope that they can use for their day to day projects. Current options are fairly expensive in the above $100 range and can be too expensive for the common hobbyist. To make this scope we want to make a BoosterPack for a common TI LaunchPad so the user would just have to buy the BoosterPack and attach it to the LaunchPad to have a high performing scope. The BoosterPack we are designing would consist of a high performance Analog to Digital Converter that can sample at high rates to measure signals up to 6.5MHz, and also include a colored screen. The user then can control the two channels on the oscilloscope with mechanical buttons and knobs attached on the LaunchPad. Overall, the results of this project could be useful to a wide scope of engineers and provide a price under $50 and a reliable measuring tool that they can use on their projects.

Project Walkthrough

The client, Texas Instruments, wants a BoosterPack for their LaunchPad series that can function as an oscilloscope. This BoosterPack would be available to both hobbyists and professionals so they can easily buy and attach the BoosterPack to a current LaunchPad board. This BoosterPack must be high performance so it is better than a typical microcontroller and be a cheap oscilloscope. To do this we will use a TI ADC that can sample at 65 MSPS. This BoosterPack must have two channels that are able to measure signals and display them on a touchless colored display. The BoosterPack will be powered by a 5V source converted from wall power. The user should also be able to input using mechanical switches that exist near the edge of the display. Standard 1MΩ 10x probes can be attached through a BNC connector for the user to measure signals. The input signals range from +15V to -15V for signal data and up to 6.5MHz in frequency. The client would like all of the hardware design files, microcontroller software, and a user’s manual. TI would also like a working prototype to show off the feasibility of the project.

Stakeholder Analysis
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

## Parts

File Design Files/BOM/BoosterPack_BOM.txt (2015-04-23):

Partlist exported from C:/Users/Eric/Desktop/Team04ScopeBoosterpack/ProjectFiles/Design Files/Schematics/boosterpack_0v1_EAGLE_sch.sch at 4/23/2015 1:21:57 PM

Part       Value          Device                 Package            Description                          C     DATASHEETURL                      DESCRIPTION                                                              FAMILY_NAME                  GENERIC_PART_NUMBER INDUSTRY_STD_PKG_TYPE MANUFACTURER      MANUFACTURER_PART_NUMBER MF               MPN       OC_FARNELL OC_NEWARK PACKAGE PACKAGE_DESIGNATOR PIN_COUNT SUPPLIER          VENDOR           
-5V_SUPPLY TL7660_D_8     TL7660_D_8             D8                                                            http://www.ti.com/lit/gpn/TL7660  CMOS Voltage Converter                                                   LOW POWER                    TL7660              SOIC                  Texas Instruments tl7660_d_8                                                                       D                  8                           Texas Instruments
A1                        HEADER4X10-BOOSTERPACK 4X10-BOOSTERPACK                                                                                                                                                                                                                                                                                                                                                                                                   
A2                        HEADER4X10-BOOSTERPACK 4X10-BOOSTERPACK                                                                                                                                                                                                                                                                                                                                                                                                   
AVERAGER   OPA890_DBV_6   OPA890_DBV_6           DBV6                                                          http://www.ti.com/lit/gpn/OPA890  Low Power, Wideband, Voltage Feedback Operational Amplifier with Disable VOLTAGE FEEDBACK             OPA890              SOT-23                Texas Instruments opa890_dbv_6                                                                     DBV                6                           Texas Instruments
C1         0.1uF          C-USC0603              C0603              CAPACITOR, American symbol                                                                                                                                                                                                                                                                                                                                                                      
C2         0.1uF          C-USC0603              C0603              CAPACITOR, American symbol                                                                                                                                                                                                                                                                                                                                                                      
C3         0.1uF          C-USC0603              C0603              CAPACITOR, American symbol                                                                                                                                                                                                                                                                                                                                                                      
C4         0.1uF          C-USC0603              C0603              CAPACITOR, American symbol                                                                                                                                                                                                                                                                                                                                                                      
C5         10u            C-USC0805              C0805              CAPACITOR, American symbol           10uF                                                                                                                                                                                                                                                                                                                                                       
C6         0.1u           C-USC0805              C0805              CAPACITOR, American symbol                                                                                                                                                                                                                                                                                                                                                                      
C7         2.2u           C-USC0805              C0805              CAPACITOR, American symbol                                                                                                                                                                                                                                                                                                                                                                      
C8         0.1u           C-USC0805              C0805              CAPACITOR, American symbol                                                                                                                                                                                                                                                                                                                                                                      
C9         2.2u           C-USC0805              C0805              CAPACITOR, American symbol                                                                                                                                                                                                                                                                                                                                                                      
C10        1000p          C-USC0805              C0805              CAPACITOR, American symbol                                                                                                                                                                                                                                                                                                                                                                      
C11        1000p          C-USC0805              C0805              CAPACITOR, American symbol                                                                                                                                                                                                                                                                                                                                                                      
C12        1000p          C-USC0805              C0805              CAPACITOR, American symbol                                                                                                                                                                                                                                                                                                                                                                      
C13        1000p          C-USC0805              C0805              CAPACITOR, American symbol                                                                                                                                                                                                                                                                                                                                                                      
C14        1000p          C-USC0805              C0805              CAPACITOR, American symbol                                                                                                                                                                                                                                                                                                                                                                      
C15        1000p          C-USC0805              C0805              CAPACITOR, American symbol                                                                                                                                                                                                                                                                                                                                                                      
C16        1000p          C-USC0805              C0805              CAPACITOR, American symbol                                                                                                                                                                                                                                                                                                                                                                      
C17        1000p          C-USC0805              C0805              CAPACITOR, American symbol                                                                                                                                                                                                                                                                                                                                                                      
C18        0.1u           C-USC0805              C0805              CAPACITOR, American symbol           0.1uF                                                                                                                                                                                                                                                                                                                                                      
C19        1000p          C-USC0805              C0805              CAPACITOR, American symbol                                                                                                                                                                                                                                                                                                                                                                      
C20        1000p          C-USC0805              C0805              CAPACITOR, American symbol                                                                                                                                                                                                                                                                                                                                                                      
C21        1000p          C-USC0805              C0805              CAPACITOR, American symbol                                                                                                                                                                                                                                                                                                                                                                      
C22        1000p          C-USC0805              C0805              CAPACITOR, American symbol                                                                                                                                                                                                                                                                                                                                                                      
C23        1000p          C-USC0805              C0805              CAPACITOR, American symbol                                                                                                                                                                                                                                                                                                                                                                      
C24        1000p          C-USC0805              C0805              CAPACITOR, American symbol                                                                                                                                                                                                                                                                                                                                                                      
C25        10uf           C-USC0805              C0805              CAPACITOR, American symbol                                                                                                                                                                                                                                                                                                                                                                      
C26        10uf           C-USC0805              C0805              CAPACITOR, American symbol                                                                                                                                                                                                                                                                                                                                                                      
C27        1000p          C-USC0805              C0805              CAPACITOR, American symbol                                                                                                                                                                                                                                                                                                                                                                      
COMPARATOR OPA890_DBV_6   OPA890_DBV_6           DBV6                                                          http://www.ti.com/lit/gpn/OPA890  Low Power, Wideband, Voltage Feedback Operational Amplifier with Disable VOLTAGE FEEDBACK             OPA890              SOT-23                Texas Instruments opa890_dbv_6                                                                     DBV                6                           Texas Instruments
JP1                       PINHD-1X1              1X01               Pin header 1x1 for 0.1" spacing                                                                                                                                                                                                                                                                                                                                                                 
OFFSET     OPA890_DBV_6   OPA890_DBV_6           DBV6                                                          http://www.ti.com/lit/gpn/OPA890  Low Power, Wideband, Voltage Feedback Operational Amplifier with Disable VOLTAGE FEEDBACK             OPA890              SOT-23                Texas Instruments opa890_dbv_6                                                                     DBV                6                           Texas Instruments
R1         2              R-US_R0805             R0805              RESISTOR, American symbol                                                                                                                                                                                                                                                                                                                                                                       
R2         2              R-US_R0805             R0805              RESISTOR, American symbol                                                                                                                                                                                                                                                                                                                                                                       
R3         56k            R-US_R0805             R0805              RESISTOR, American symbol                                                                                                                                                                                                                                                                                                                                                                       
R4         50             R-US_R0805             R0805              RESISTOR, American symbol                                                                                                                                                                                                                                                                                                                                                                       
R5         50             R-US_R0805             R0805              RESISTOR, American symbol                                                                                                                                                                                                                                                                                                                                                                       
R6         50             R-US_R0805             R0805              RESISTOR, American symbol                                                                                                                                                                                                                                                                                                                                                                       
R7         1k             R-US_R0805             R0805              RESISTOR, American symbol                                                                                                                                                                                                                                                                                                                                                                       
R8         200            R-US_R0805             R0805              RESISTOR, American symbol                                                                                                                                                                                                                                                                                                                                                                       
R9         75             R-US_R0805             R0805              RESISTOR, American symbol                                                                                                                                                                                                                                                                                                                                                                       
R10        300            R-US_R0805             R0805              RESISTOR, American symbol                                                                                                                                                                                                                                                                                                                                                                       
R11        50             R-US_R0805             R0805              RESISTOR, American symbol                                                                                                                                                                                                                                                                                                                                                                       
R12        75             R-US_R0805             R0805              RESISTOR, American symbol                                                                                                                                                                                                                                                                                                                                                                       
R13        75             R-US_R0805             R0805              RESISTOR, American symbol                                                                                                                                                                                                                                                                                                                                                                       
R14        1k             R-US_R0805             R0805              RESISTOR, American symbol                                                                                                                                                                                                                                                                                                                                                                       
R15        1k             R-US_R0805             R0805              RESISTOR, American symbol                                                                                                                                                                                                                                                                                                                                                                       
R16        1k             R-US_R0805             R0805              RESISTOR, American symbol                                                                                                                                                                                                                                                                                                                                                                       
R17        1k             R-US_R0805             R0805              RESISTOR, American symbol                                                                                                                                                                                                                                                                                                                                                                       
R18        1k             R-US_R0805             R0805              RESISTOR, American symbol                                                                                                                                                                                                                                                                                                                                                                       
R19        1k             R-US_R0805             R0805              RESISTOR, American symbol                                                                                                                                                                                                                                                                                                                                                                       
R20        1k             R-US_R0805             R0805              RESISTOR, American symbol                                                                                                                                                                                                                                                                                                                                                                       
R21        1k             R-US_R0805             R0805              RESISTOR, American symbol                                                                                                                                                                                                                                                                                                                                                                       
R22        300            R-US_R0805             R0805              RESISTOR, American symbol                                                                                                                                                                                                                                                                                                                                                                       
R23        75             R-US_R0805             R0805              RESISTOR, American symbol                                                                                                                                                                                                                                                                                                                                                                       
R24        10k            R-TRIMM64W             RTRIM64W           Trimm resistor                                                                                                                                                                                                                                                                                                                                                                                  
R25        1k             R-US_M0805             M0805              RESISTOR, American symbol                                                                                                                                                                                                                                                                                                                                                                       
R26        1k             R-US_M0805             M0805              RESISTOR, American symbol                                                                                                                                                                                                                                                                                                                                                                       
R27        1k             R-US_M0805             M0805              RESISTOR, American symbol                                                                                                                                                                                                                                                                                                                                                                       
R28        7.5k           R-US_M0805             M0805              RESISTOR, American symbol                                                                                                                                                                                                                                                                                                                                                                       
R29        2.5k           R-US_M0805             M0805              RESISTOR, American symbol                                                                                                                                                                                                                                                                                                                                                                       
R30        10k            R-US_M0805             M0805              RESISTOR, American symbol
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

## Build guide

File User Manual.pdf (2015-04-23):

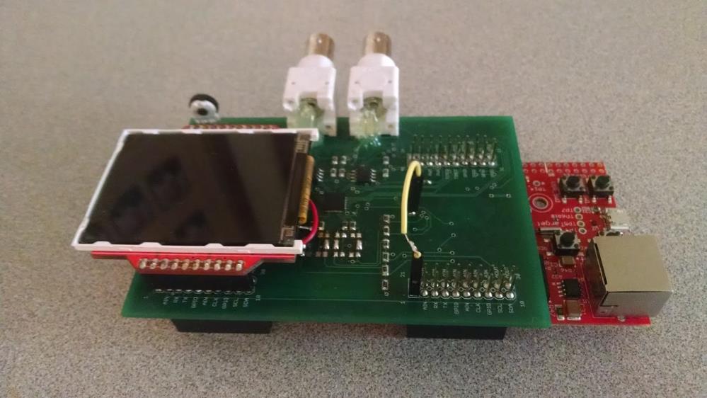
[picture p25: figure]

# TI BoosterPack Oscilloscope

## User Manual 1.0

Eric Taylor and Raymond Montgomery | Rose-Hulman | Texas Instruments | Spring 2015

## Purpose

The purpose of this user manual is to help you get started setting up and getting familiar with the project. This assumes that you have the board already constructed from the board files on GitHub using the BOM also on GitHub. This will also include how to improve upon this project and traverse the files on GitHub .

## Table of Contents

Hardware Set-Up | 3
− | Color LCD Modifications | 3
− | Oscilloscope Board Jumper and Passive Filter | 3
− | Tiva C Connected LaunchPad | 4
Software Setup | 4
Usage of the Scope | 5
TODOs | 5
GitHub | 5

## 1.0 Hardware Set-Up

To set up the hardware you need three things:

- 2.2" Color LCD BoosterPack Kit by RobG
- A Fabricated and Populated Oscilloscope PCB
- Tiva C Connected LaunchPad

1.1 Color LCD Modifications

To make use of the EPI interface a small modification had to be made to the LCD BoosterPack hardware. You have to make sure neither jumper is soldered on the D/C pin, and then attach a wire to the middle pad and connect it to pad JP5. A picture showing this is below.

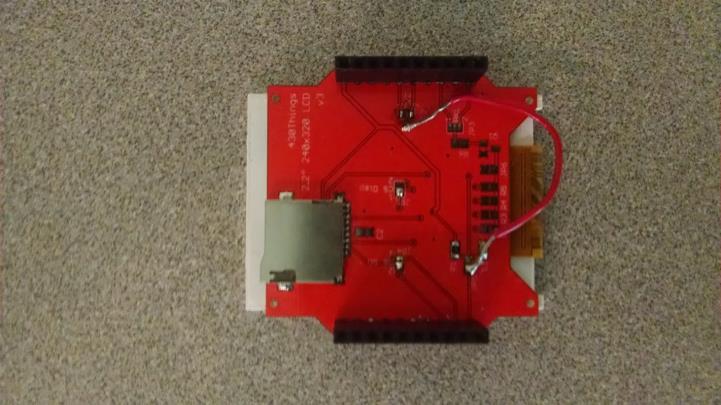
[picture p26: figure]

1.2 Oscilloscope Board Jumper and Passive Filter

For the purposes of debugging a pin was left exposed on the ADC for this first revision. Next revisions should connect this pin to the standard LDD for the ADC. (Connect VDRV to VDD in the EAGLE files). This jumper is necessary to power the ADC. A typical female-to-female jumper was used. A picture showing it is seen below. (The Yellow Wire). Also leave passive filter disconnected and solder the cap connections so the signal can continue through. More explanation in TODO.

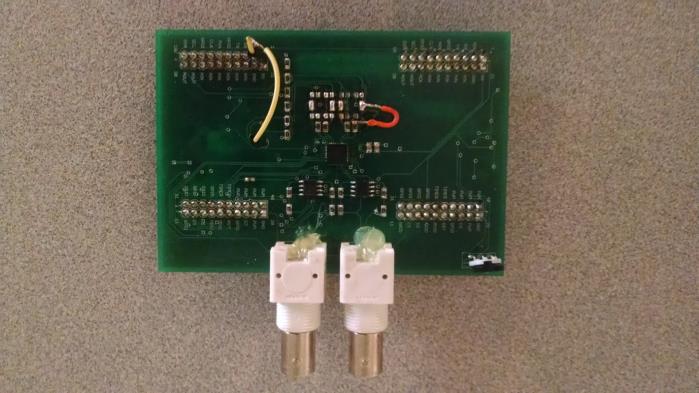
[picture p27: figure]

*Note - Orange Wire is there because of mistake while soldering

1.3 Tiva C Connected LaunchPad

No modifications should be needed. Make sure jumpers are connected like below.

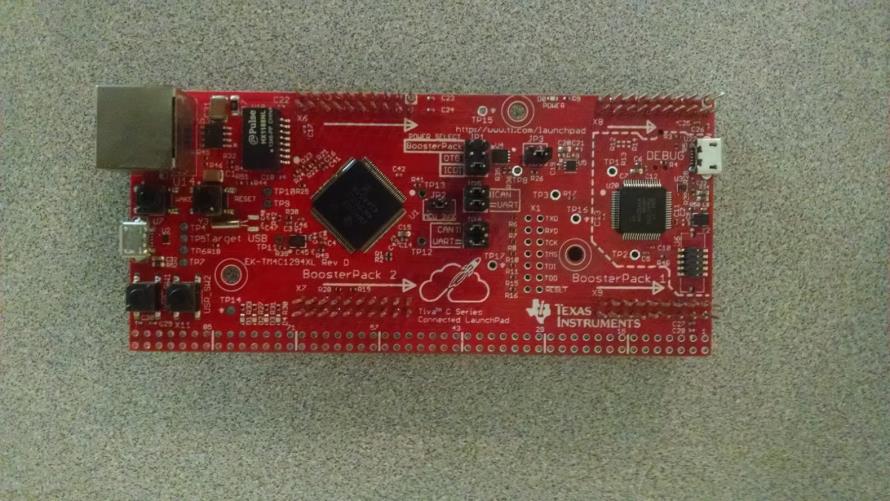
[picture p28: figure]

Once all hardware is setup, you can attach all of the pieces as seen on the first page.

## 2.0 Software Setup

Four things are needed for the software setup.

- Energia w/ Tiva C Drivers
- Senior_Project_Main.ino (on GitHub under Software Code)
- Screen_ILI9340_Library.cpp/h

Minimal Setup is needed. First download Energia and put the screen driver and header files in the following path. (Note: The drivers are edited from the original online to account for the one pin being moved across the board.)

..\energia-0101E0013\hardware\lm4f\libraries\

Then open Senior_Project_Main.ino and select Tiva C tm4c129 as the board, Finally compile and run.

## 3.0 Usage of the Scope

1. To use the scope you can use any BNC connector or 1x probe. However 10x probes did not work when tested with the system. Connect probes up like a typical scope. For this revision you can only trigger of one channel. (BNC away from Screen).
2. Only signals from +/- 1.5 can be inputted at the end of the probe.
3. Power can be supplied through any micro USB source. Portable battery or laptop will work.
4. The trigger level can be adjusted using the potentiometer. Then the voltage per deviation and time per deviation can be adjusted using the two user buttons on the LaunchPad.

Note: The GUI is still in its early stages and can be improved upon.

## 4.0 TODOs

This section contains improvements that can be made on this project and steps to continue its development.

1. Switch BNC connections so that they are vertical. They are currently unstable.
2. Add buffer to front end so that 10x probes cannot load circuit.
3. Add switchable attenuator to front end.
4. Add uDMA to software to collect samples faster and be able to achieve full 7 MHz bandwidth . Currently a timer interrupt is used and the bandwidth is about 200kHz.
5. Put 10MHz flat pass band active filter instead of current passive filter.

## 5.0 GitHub

On GitHub you can find a directory listing on the front page giving explanation to the file directory and source files.

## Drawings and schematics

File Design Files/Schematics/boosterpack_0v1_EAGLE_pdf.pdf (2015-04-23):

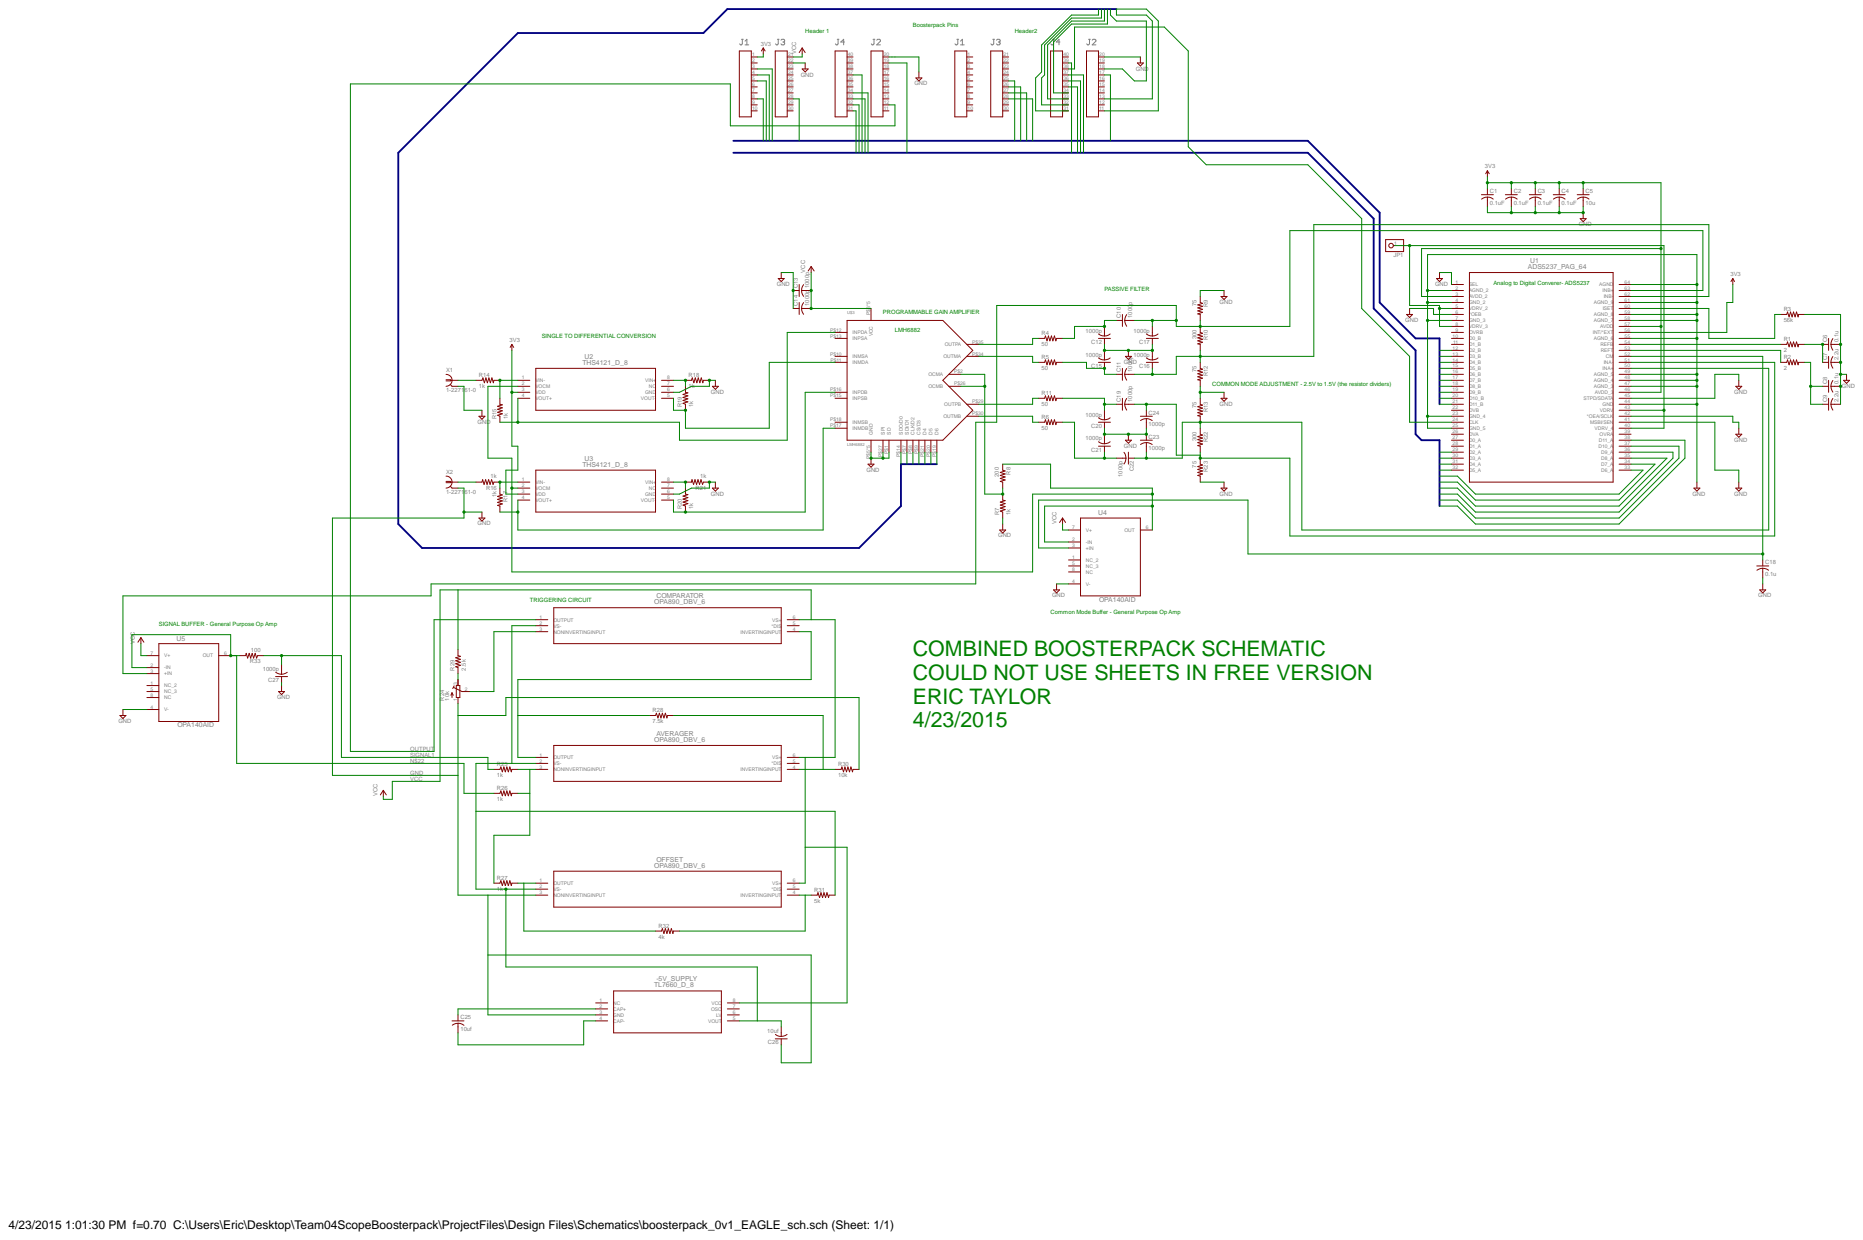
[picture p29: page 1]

Analog to Digital Converer- ADS5237

SINGLE TO DIFFERENTIAL CONVERSION

VDD 3

INPDB P$16

COMMON MODE ADJUSTMENT - 2.5V to 1.5V (the resistor dividers)

Common Mode Buffer - General Purpose Op Amp

SIGNAL BUFFER - General Purpose Op Amp
U5

COMBINED BOOSTERPACK SCHEMATIC
COULD NOT USE SHEETS IN FREE VERSION
ERIC TAYLOR

4/23/2015 1:01:30 PM f=0.70 C:\Users\Eric\Desktop\Team04ScopeBoosterpack\ProjectFiles\Design Files\Schematics\boosterpack_0v1_EAGLE_sch.sch (Sheet: 1/1)

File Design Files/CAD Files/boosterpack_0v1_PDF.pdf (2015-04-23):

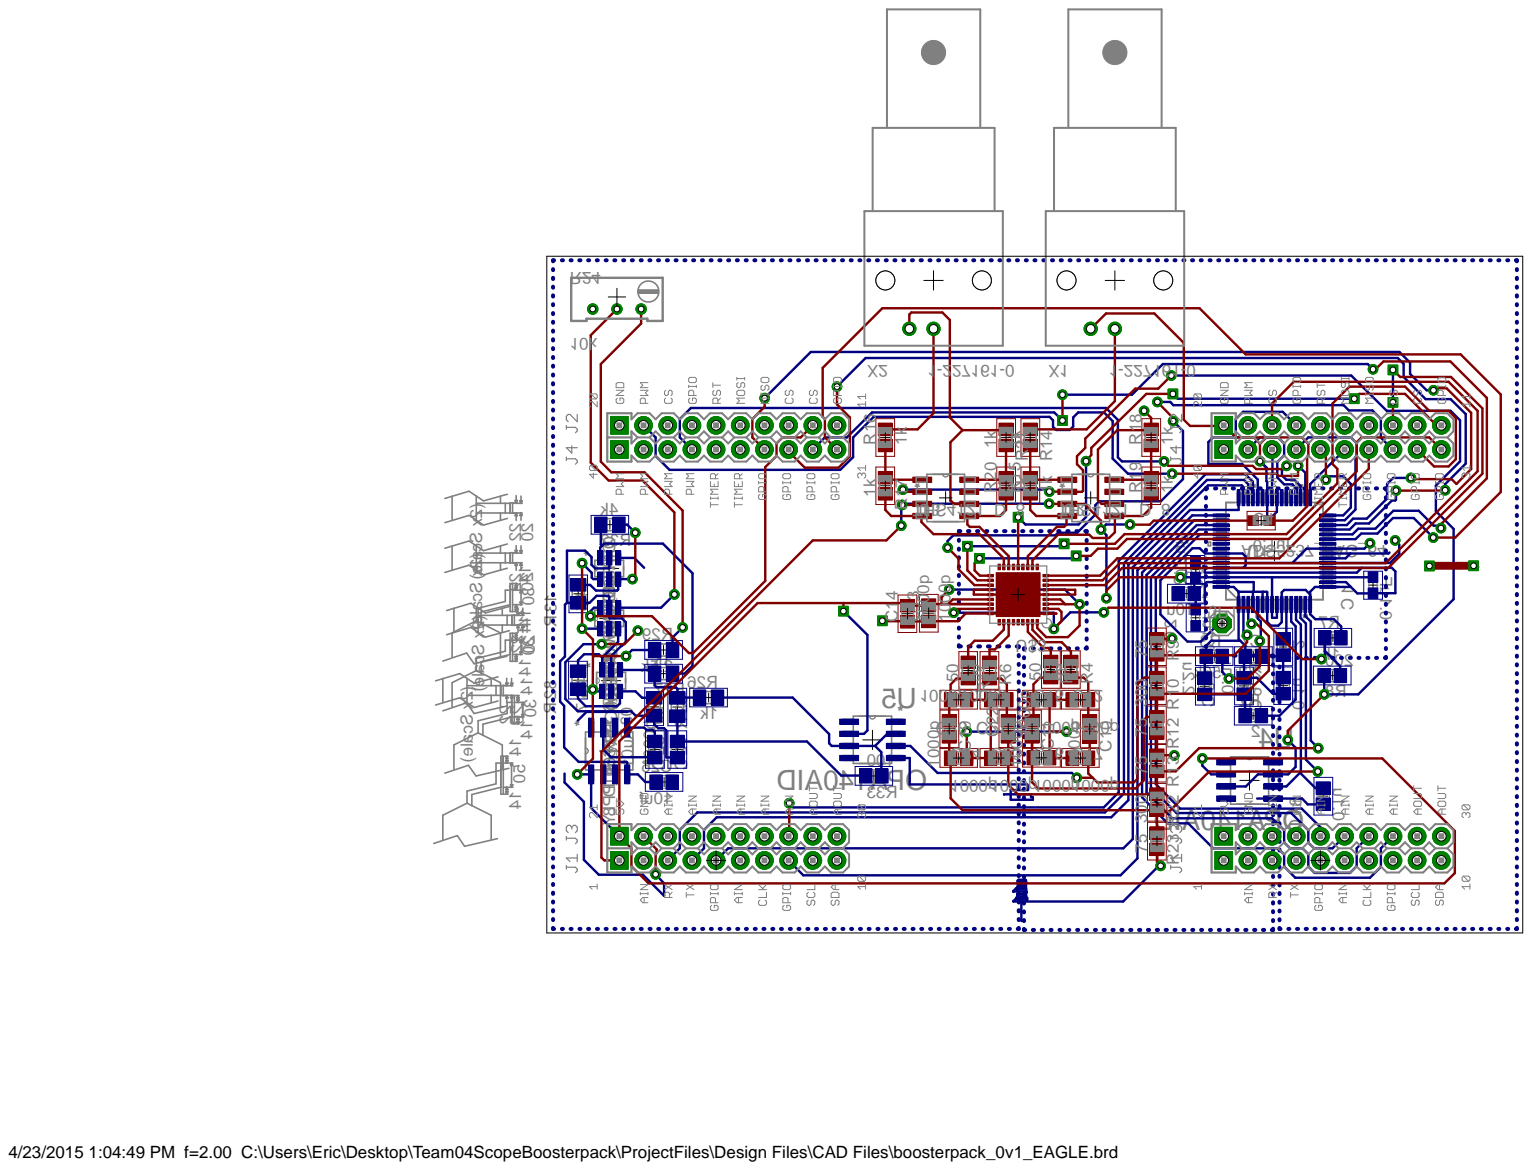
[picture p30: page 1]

4/23/2015 1:04:49 PM f=2.00 C:\Users\Eric\Desktop\Team04ScopeBoosterpack\ProjectFiles\Design Files\CAD Files\boosterpack_0v1_EAGLE.brd

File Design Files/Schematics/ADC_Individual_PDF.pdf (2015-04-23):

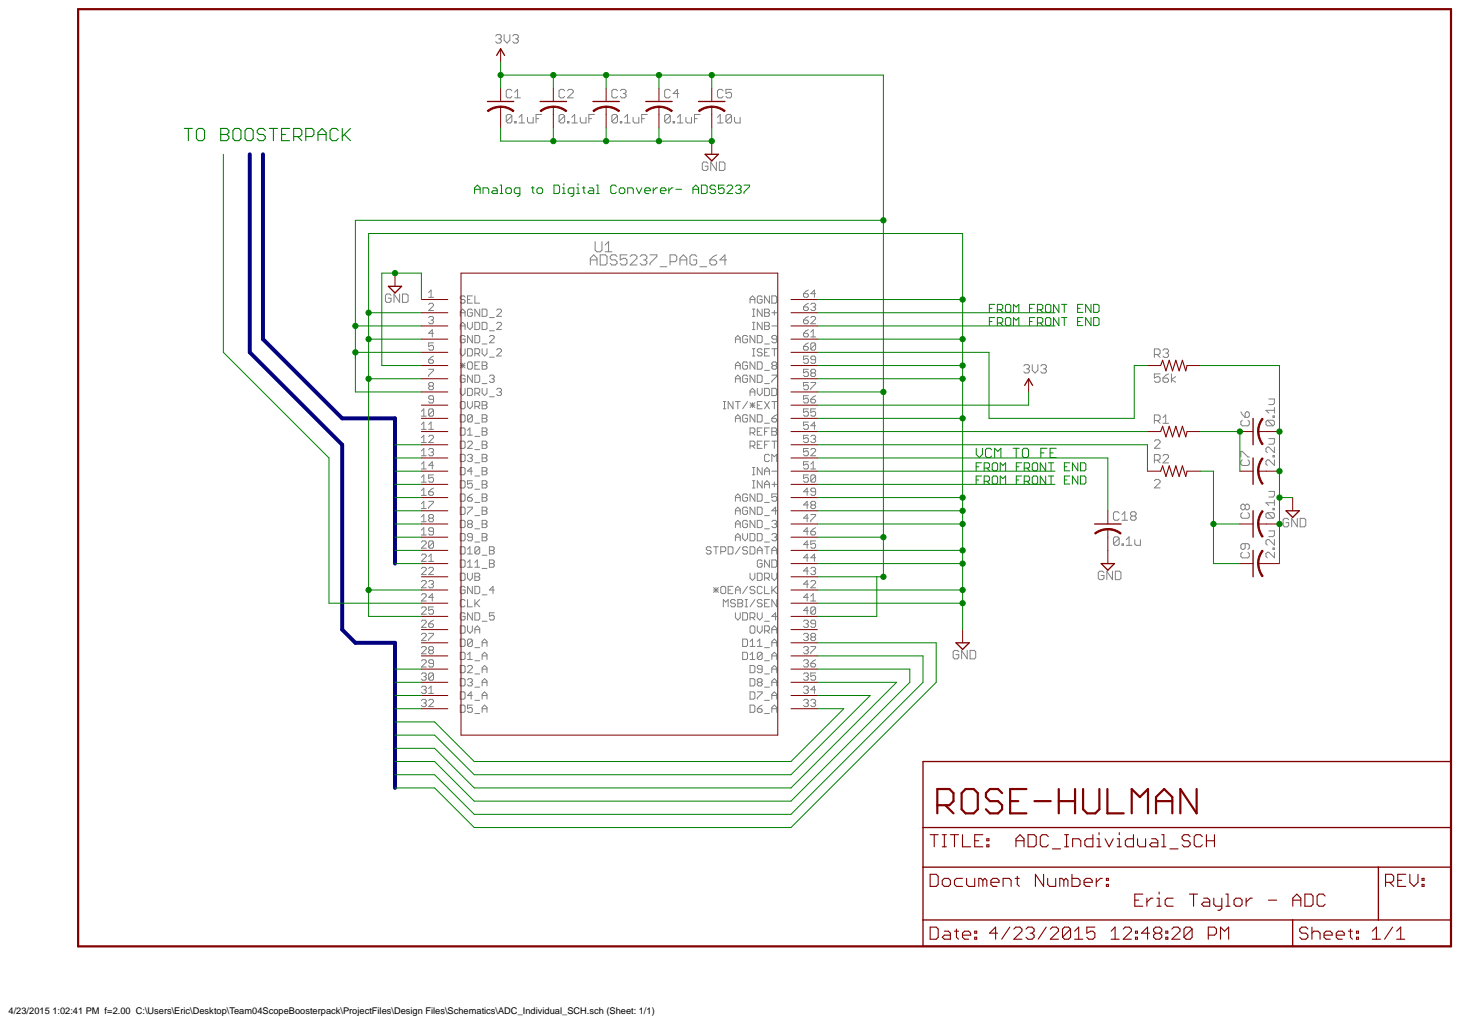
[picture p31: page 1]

4/23/2015 1:02:41 PM f=2.00 C:\Users\Eric\Desktop\Team04ScopeBoosterpack\ProjectFiles\Design Files\Schematics\ADC_Individual_SCH.sch (Sheet: 1/1)

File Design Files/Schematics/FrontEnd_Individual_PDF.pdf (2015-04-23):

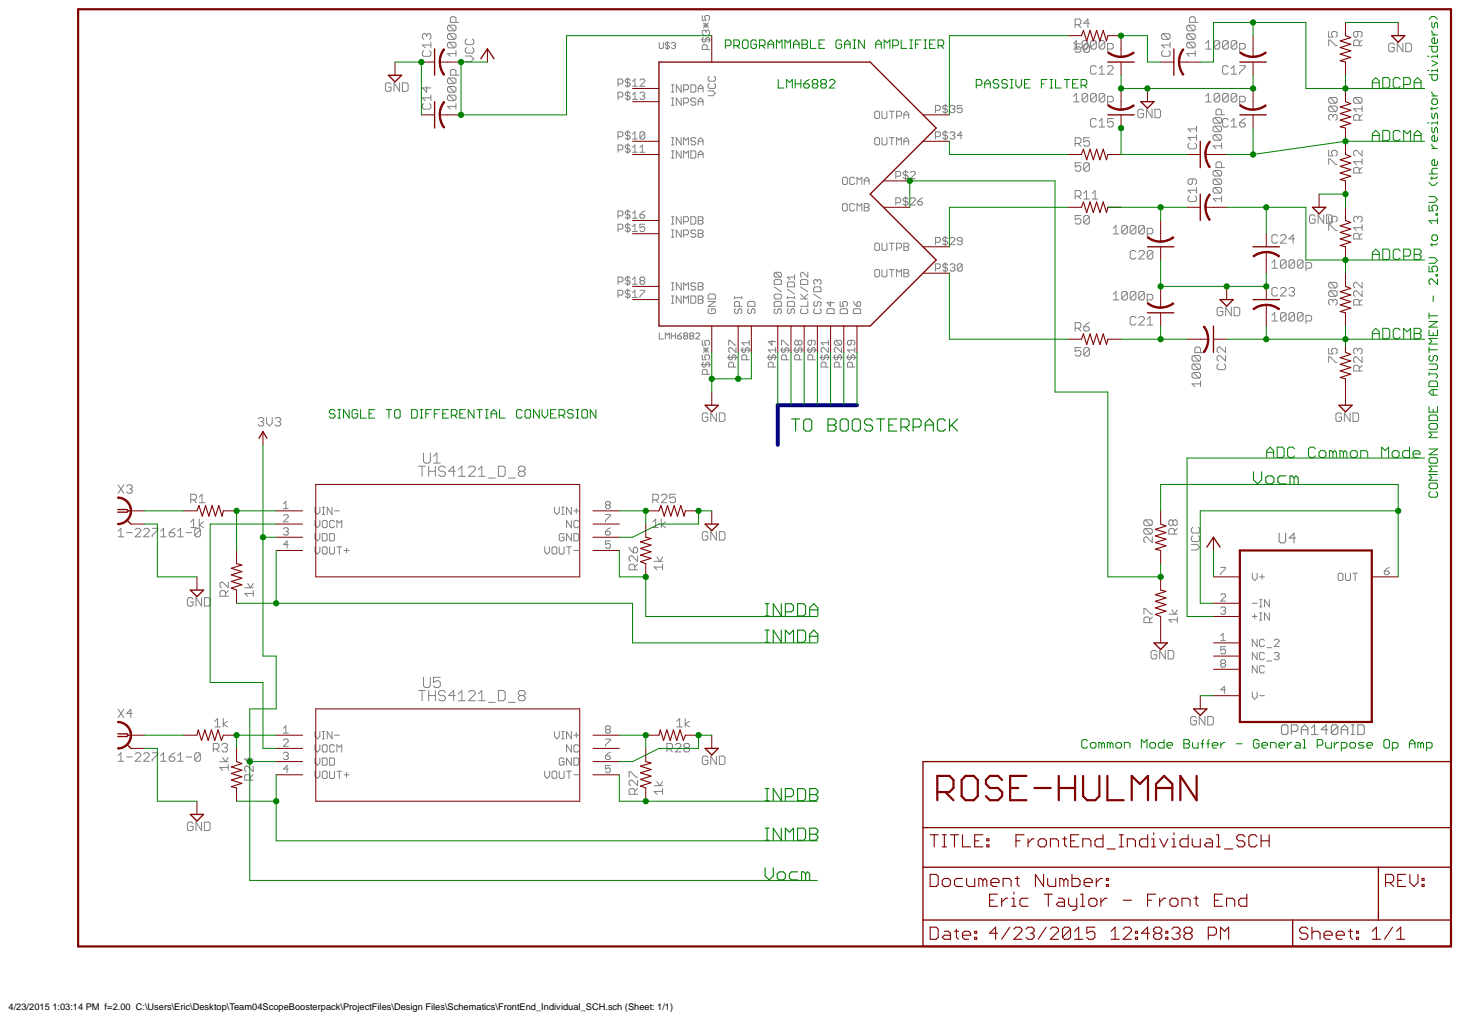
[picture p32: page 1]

4/23/2015 1:03:14 PM f=2.00 C:\Users\Eric\Desktop\Team04ScopeBoosterpack\ProjectFiles\Design Files\Schematics\FrontEnd_Individual_SCH.sch (Sheet: 1/1)

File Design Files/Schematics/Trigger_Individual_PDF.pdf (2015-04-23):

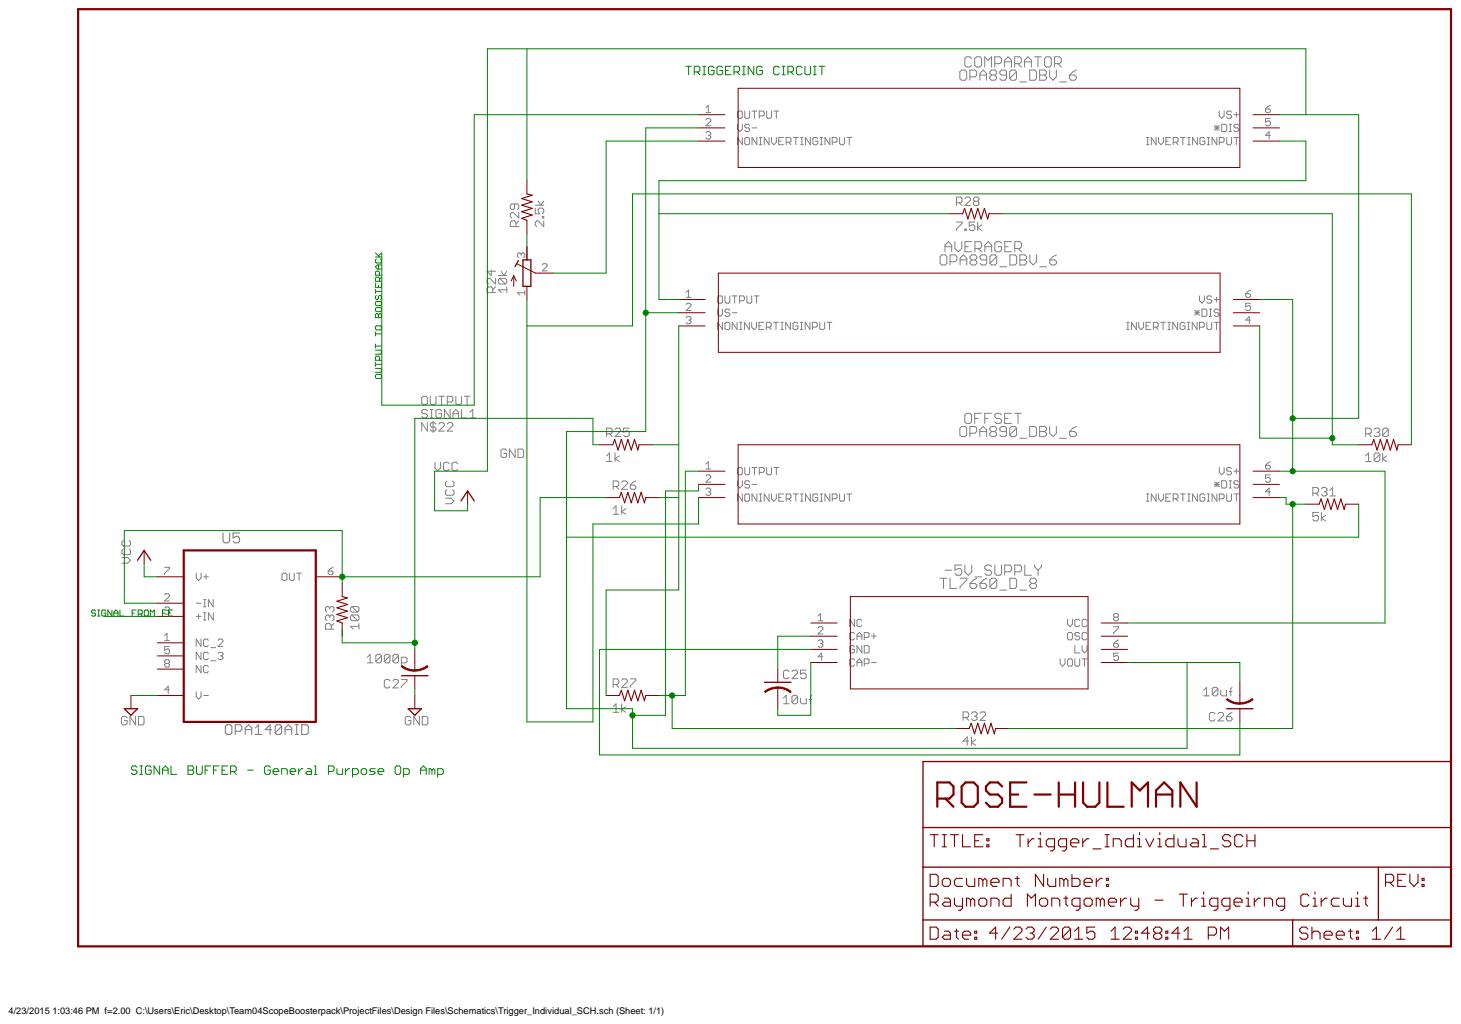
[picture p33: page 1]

4/23/2015 1:03:46 PM f=2.00 C:\Users\Eric\Desktop\Team04ScopeBoosterpack\ProjectFiles\Design Files\Schematics\Trigger_Individual_SCH.sch (Sheet: 1/1)

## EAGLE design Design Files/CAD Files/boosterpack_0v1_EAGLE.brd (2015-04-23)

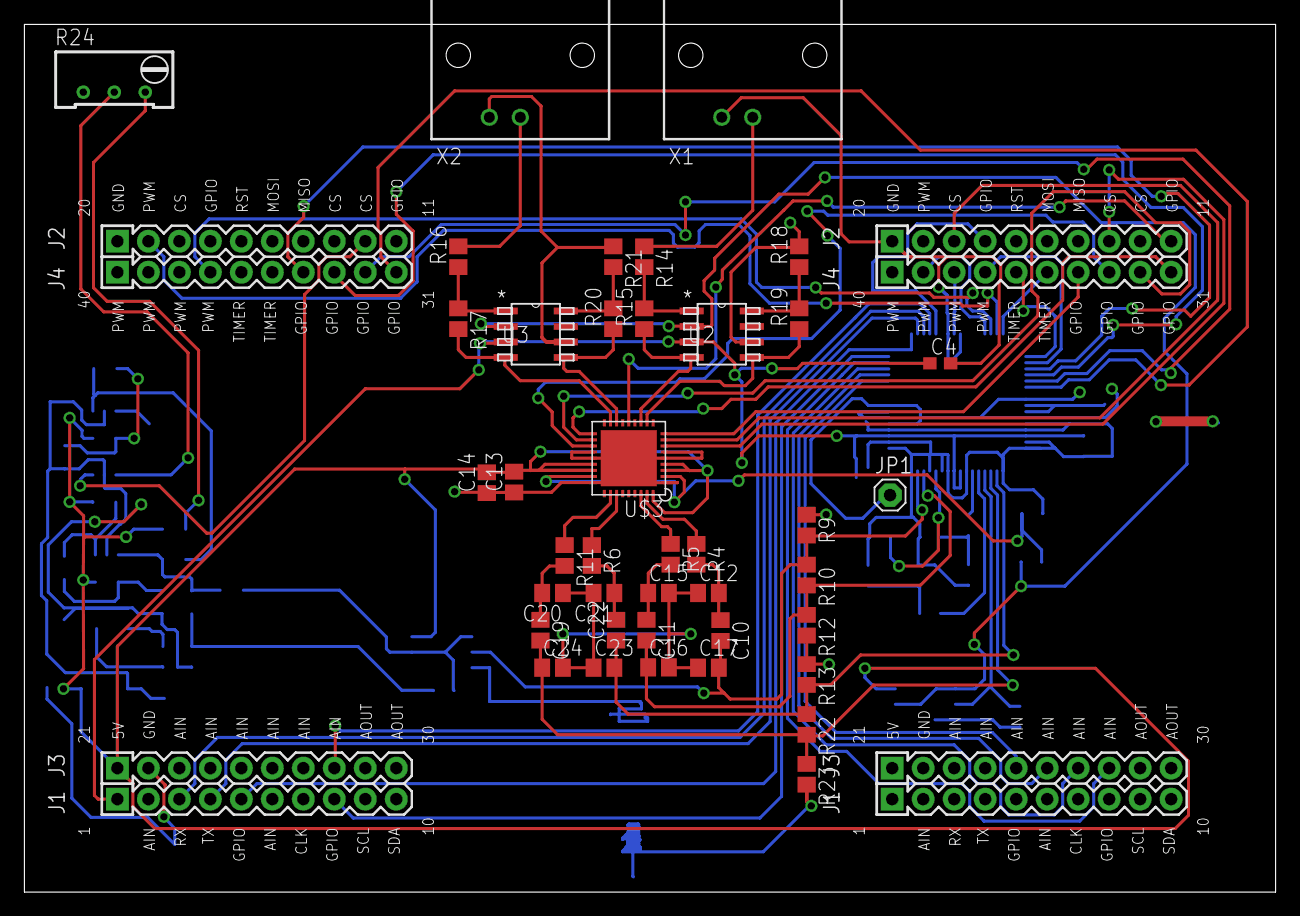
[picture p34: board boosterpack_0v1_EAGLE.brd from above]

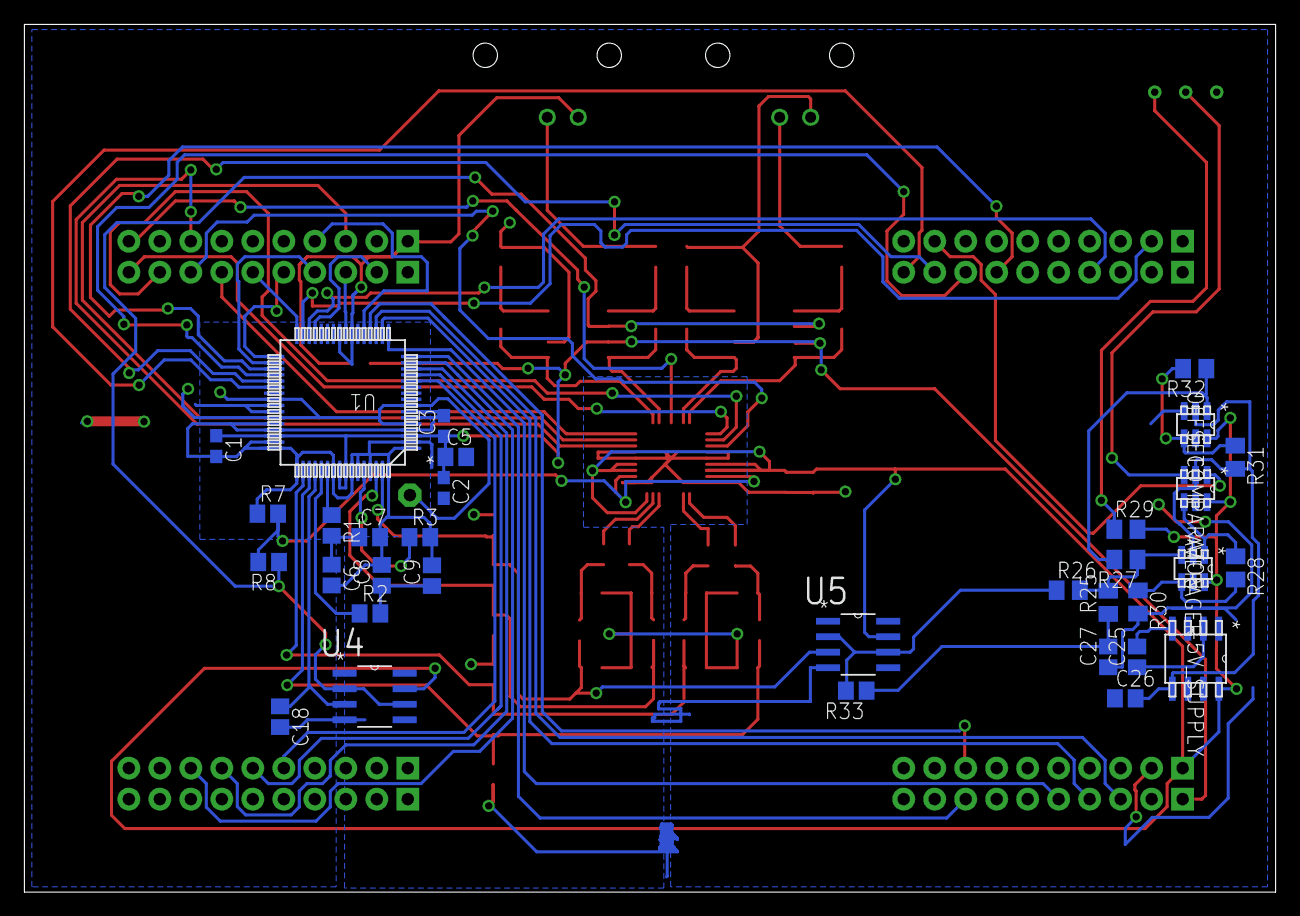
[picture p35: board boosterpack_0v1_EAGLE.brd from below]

Board: 2 copper layers, 102.5 x 71.1 mm, 75 parts (33 on the bottom side), 75 nets.

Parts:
-5V_SUPPLY: TL7660_D_8; D8
A1, A2: 4X10-BOOSTERPACK
AVERAGER: OPA890_DBV_6; DBV6
C1, C2, C3, C4: 0.1uF; C0603
C5: 10u; C0805
C6, C8, C18: 0.1u; C0805
C7, C9: 2.2u; C0805
C10, C11, C12, C13, C14, C15, C16, C17, C19, C20, C21, C22, C23, C24, C27: 1000p; C0805
C25, C26: 10uf; C0805
COMPARATOR: OPA890_DBV_6; DBV6
JP1: 1X01
OFFSET: OPA890_DBV_6; DBV6
R1, R2: 2; R0805
R3: 56k; R0805
R4, R5, R6, R11: 50; R0805
R7, R14, R15, R16, R17, R18, R19, R20, R21: 1k; R0805
R8: 200; R0805
R9, R12, R13, R23: 75; R0805
R10, R22: 300; R0805
R24: 10k; RTRIM64W
R25, R26, R27: 1k; M0805
R28: 7.5k; M0805
R29: 2.5k; M0805
R30: 10k; M0805
R31: 5k; M0805
R32: 4k; M0805
R33: 100; R0805
U1: ADS5237_PAG_64; PAG64
U2, U3: THS4121_D_8; D8
U4, U5: OPA140AID; SOIC127P600X175-8N
U$3: LMH6882; WQFN-36-NJK
X1, X2: 1-227161-0; AMP_227161

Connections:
3.3V: A2.1, C1.1, C2.1, C3.1, C4.1, C5.1, U1.3, U1.46, U1.56, U1.57, U2.3, U3.3
A0: A1.25, U1.12
A1: A1.26, U1.13
A2: A1.27, U1.14
A3: A1.28, U1.15
A4: A2.8, U1.16
A5: A2.5, U1.17
A6: A2.4, U1.18
A7: A2.3, U1.19
A8: A2.28, U1.20
A9: A1.17, U1.21
B0: A1.39, U1.29
B1: A2.37, U1.30
B2: A2.19, U1.31
B3: A1.35, U1.32
B4: A1.36, U1.33
B5: A1.37, U1.34
B6: A2.34, U1.35
B7: A2.33, U1.36
B8: A2.32, U1.37
B9: A2.31, U1.38
C0: A1.11, U$3.P$14
C1: A1.13, U$3.P$7
C2: A1.18, U$3.P$8
C3: A1.34, U$3.P$9
C4: A1.33, U$3.P$21
C5: A1.32, U$3.P$20
C6: A1.31, U$3.P$19
GND: -5V_SUPPLY.3, A1.20, A2.20, A2.22, C1.2, C2.2, C3.2, C4.2, C5.2, C6.2, C7.2, C8.2, C9.2, C12.1, C13.1, C14.1, C15.2, C16.2, C17.1, C18.2, C20.1, C21.2, C23.1, C24.2, C26.1, C27.1, OFFSET.3, R3.2, R7.1, R9.1, R12.2, R13.1, R18.2, R21.1, R23.2, R24.1, R30.2, U1.1, U1.2, U1.4, U1.6, U1.7, U1.23, U1.25, U1.41, U1.42, U1.44, U1.45, U1.47, U1.48, U1.49, U1.55, U1.58, U1.59, U1.61, U1.64, U2.6, U3.6, U4.4, U5.4, U$3.P$1, U$3.P$5, U$3.P$6, U$3.P$22, U$3.P$23, U$3.P$27, U$3.TH, X1.2, X2.2
unnamed: A1.38, U1.24
unnamed: JP1.1, U1.5, U1.8, U1.40, U1.43
unnamed: C18.1, U1.52, U4.3
unnamed: C19.2, C24.1, R22.2, R23.1, U1.51
unnamed: R24.3, R29.1
unnamed: COMPARATOR.3, R24.2
unnamed: AVERAGER.4, R28.2, R30.1
unnamed: C11.1, C15.1, R5.2
unnamed: R8.1, U2.2, U3.2, U4.2, U4.6
unnamed: R7.2, R8.2, U$3.P$2, U$3.P$26
unnamed: AVERAGER.3, R25.2, R26.2, R27.1
unnamed: C11.2, C16.1, R10.2, R12.1, U1.62
unnamed: C21.1, C22.2, R6.2
unnamed: C19.1, C20.2, R11.2
unnamed: AVERAGER.1, COMPARATOR.4, R28.1
unnamed: C22.1, C23.2, R13.2, R22.1, U1.50
unnamed: OFFSET.1, R27.2, R32.1
unnamed: OFFSET.4, R31.1, R32.2
unnamed: R5.1, U$3.P$34
unnamed: R26.1, R33.2, U5.2, U5.6
unnamed: -5V_SUPPLY.2, C25.1
unnamed: -5V_SUPPLY.4, C25.2
unnamed: -5V_SUPPLY.5, AVERAGER.2, C26.2, COMPARATOR.2, OFFSET.2, R31.2
unnamed: C10.2, C17.2, R9.2, R10.1, U1.63, U5.3
unnamed: R4.1, U$3.P$35
unnamed: C6.1, C7.1, R1.2
unnamed: C8.1, C9.1, R2.2
unnamed: R1.1, U1.54
unnamed: R2.1, U1.53
unnamed: R3.1, U1.60
unnamed: R14.1, X1.1
unnamed: R6.1, U$3.P$30
unnamed: R14.2, R15.2, U2.1
unnamed: R15.1, U2.4, U$3.P$12
unnamed: R16.1, R17.1, U3.1
unnamed: R17.2, U3.4, U$3.P$17
unnamed: R18.1, R19.2, U2.8
unnamed: R20.2, R21.2, U3.8
unnamed: R16.2, X2.1
unnamed: R20.1, U3.5, U$3.P$16
unnamed: R19.1, U2.5, U$3.P$11
unnamed: R11.1, U$3.P$29
unnamed: C10.1, C12.2, R4.2
OUTPUT: A2.12, COMPARATOR.1
SIGNAL1: C27.2, R25.1, R33.1
VCC: -5V_SUPPLY.8, A2.21, AVERAGER.6, C13.2, C14.2, COMPARATOR.6, OFFSET.6, R29.2, U4.7, U5.7, U$3.P$3, U$3.P$4, U$3.P$24, U$3.P$25, U$3.P$36

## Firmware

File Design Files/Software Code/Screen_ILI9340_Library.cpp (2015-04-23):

//
// Screen_ILI9340_Library.cpp
// Library C++ code
// ----------------------------------
// Developed with embedXcode
// http://embedXcode.weebly.com
//
// Project LCD_screen Library Suite
//
// Created by Rei VILO, Feb 18, 2014
// http://embedXcode.weebly.com
//
//
// Copyright    © Rei VILO, 2013-2014
// License      Creative Commons
//              Attribution-NonCommercial-ShareAlike 3.0 Unported (CC BY-NC-SA 3.0)
//
//
// Library header
#include "Screen_ILI9340_Library.h"
///
#define ILINOP     0x00
#define ILISWRESET 0x01
#define ILIRDDID   0x04
#define ILIRDDST   0x09
#define ILISLPIN   0x10
#define ILISLPOUT  0x11
#define ILIPTLON   0x12
#define ILINORON   0x13
#define ILIRDMODE  0x0A
#define ILIRDMADCTL  0x0B
#define ILIRDPIXFMT  0x0C
#define ILIRDIMGFMT  0x0A
#define ILIRDSELFDIAG  0x0F
#define ILIINVOFF  0x20
#define ILIINVON   0x21
#define ILIGAMMASET 0x26
#define ILIDISPOFF 0x28
#define ILIDISPON  0x29
#define ILICASET   0x2A
#define ILIPASET   0x2B
#define ILIRAMWR   0x2C
#define ILIRAMRD   0x2E
#define ILIPTLAR   0x30
#define ILIGRAMMODE  0x36
#define DEFAULTILIGRAMMODE ILIMADCTL_BGR
#define ILIMADCTL_MY  0x80
#define ILIMADCTL_MX  0x40
#define ILIMADCTL_MV  0x20
#define ILIMADCTL_ML  0x10
#define ILIMADCTL_RGB 0x00
#define ILIMADCTL_BGR 0x08
#define ILIMADCTL_MH  0x04
#define ILIPIXFMT  0x3A
#define ILIFRMCTR1 0xB1
#define ILIFRMCTR2 0xB2
#define ILIFRMCTR3 0xB3
#define ILIINVCTR  0xB4
#define ILIDFUNCTR 0xB6
#define ILIPWCTR1  0xC0
#define ILIPWCTR2  0xC1
#define ILIPWCTR3  0xC2
#define ILIPWCTR4  0xC3
#define ILIPWCTR5  0xC4
#define ILIVMCTR1  0xC5
#define ILIVMCTR2  0xC7
#define ILIRDID1   0xDA
#define ILIRDID2   0xDB
#define ILIRDID3   0xDC
#define ILIRDID4   0xDD
#define ILIGMCTRP1 0xE0
#define ILIGMCTRN1 0xE1
#define LCD_HEIGHT      320
#define LCD_WIDTH       240
#define TOUCH_TRIM  0x00
Screen_ILI9340::Screen_ILI9340()
{
    ;
}
void Screen_ILI9340::begin()
{
    pinMode(_pinScreenCS, OUTPUT);
    pinMode(_pinSDcardCS, OUTPUT);
    pinMode(_pinScreenReset, OUTPUT);
    pinMode(_pinScreenDataCommand, OUTPUT);
    pinMode(_pinScreenReset, OUTPUT);
    digitalWrite(_pinScreenDataCommand, HIGH);
#if defined(__LM4F120H5QR__) || defined(__TM4C1230C3PM__)
    SPI.setModule(2);
    SPI.begin();
    SPI.setClockDivider(SPI_CLOCK_DIV2);
#else
    SPI.begin();
    SPI.setClockDivider(SPI_CLOCK_DIV1);
#endif
    SPI.setBitOrder(MSBFIRST);
    SPI.setDataMode(SPI_MODE0);
    delay(1);
    digitalWrite(_pinScreenReset, LOW);
    delay(10);
    digitalWrite(_pinScreenReset, HIGH);
    delay(10);
    _writeCommand8(0xEF);
    _writeData8(0x03);
    _writeData8(0x80);
    _writeData8(0x02);
    _writeCommand8(0xCF);
    _writeData8(0x00);
    _writeData8(0XC1);
    _writeData8(0X30);
    _writeCommand8(0xED);
    _writeData8(0x64);
    _writeData8(0x03);
    _writeData8(0X12);
    _writeData8(0X81);
    _writeCommand8(0xE8);
    _writeData8(0x85);
    _writeData8(0x00);
    _writeData8(0x78);
    _writeCommand8(0xCB);
    _writeData8(0x39);
    _writeData8(0x2C);
    _writeData8(0x00);
    _writeData8(0x34);
    _writeData8(0x02);
    _writeCommand8(0xF7);
    _writeData8(0x20);
    _writeCommand8(0xEA);
    _writeData8(0x00);
    _writeData8(0x00);
    _writeCommand8(ILIPWCTR1);
    _writeData8(0x23);
    _writeCommand8(ILIPWCTR2);
    _writeData8(0x10);
    _writeCommand8(ILIVMCTR1);
    _writeData8(0x3e);
    _writeData8(0x28);
    _writeCommand8(ILIVMCTR2);
    _writeData8(0x86);
    _writeCommand8(ILIGRAMMODE);
    _writeData8(DEFAULTILIGRAMMODE);
    _writeCommand8(ILIPIXFMT);
    _writeData8(0x55);
    _writeCommand8(ILIFRMCTR1);
    _writeData8(0x00);
    _writeData8(0x18);
    _writeCommand8(ILIDFUNCTR);
    _writeData8(0x08);
    _writeData8(0x82);
    _writeData8(0x27);
    _writeCommand8(0xF2);
    _writeData8(0x00);
    _writeCommand8(ILIGAMMASET);
    _writeData8(0x01);
    _writeCommand8(ILIGMCTRP1);
    _writeData8(0x0F);
    _writeData8(0x31);
    _writeData8(0x2B);
    _writeData8(0x0C);
    _writeData8(0x0E);
    _writeData8(0x08);
    _writeData8(0x4E);
    _writeData8(0xF1);
    _writeData8(0x37);
    _writeData8(0x07);
    _writeData8(0x10);
    _writeData8(0x03);
    _writeData8(0x0E);
    _writeData8(0x09);
    _writeData8(0x00);
    _writeCommand8(ILIGMCTRN1);
    _writeData8(0x00);
    _writeData8(0x0E);
    _writeData8(0x14);
    _writeData8(0x03);
    _writeData8(0x11);
    _writeData8(0x07);
    _writeData8(0x31);
    _writeData8(0xC1);
    _writeData8(0x48);
    _writeData8(0x08);
    _writeData8(0x0F);
    _writeData8(0x0C);
    _writeData8(0x31);
    _writeData8(0x36);
    _writeData8(0x0F);
    _writeCommand8(ILISLPOUT);
    delay(120);
    _writeCommand8(ILIDISPON);
    _writeCommand8(ILIINVOFF);
    _writeRegister8(0x55, 0x01);
    _screenWidth = LCD_WIDTH;
    _screenHeigth = LCD_HEIGHT;
    _screenDiagonal = 22;
    _penSolid  = false;
    _fontSolid = true;
    setOrientation(0);
    clear();
}
String Screen_ILI9340::WhoAmI()
{
    return "LCD 2.2\" + SD BoosterPack";
}
void Screen_ILI9340::_setOrientation(uint8_t orientation)
{
    switch (_orientation) {
        case 0:
            _writeRegister8(ILIGRAMMODE, 0b01000000 | DEFAULTILIGRAMMODE);
            break;
        case 1:
            _writeRegister8(ILIGRAMMODE, 0b00100000 | DEFAULTILIGRAMMODE);
            break;
        case 2:
            _writeRegister8(ILIGRAMMODE, 0b10000000 | DEFAULTILIGRAMMODE);
            break;
        case 3:
            _writeRegister8(ILIGRAMMODE, 0b11100000 | DEFAULTILIGRAMMODE);
            break;
    }
}
void Screen_ILI9340::_writeCommand8(uint8_t command8)
{
    digitalWrite(_pinScreenDataCommand, LOW);
    digitalWrite(_pinScreenCS, LOW);
    SPI.transfer(command8);
    digitalWrite(_pinScreenCS, HIGH);
    digitalWrite(_pinScreenDataCommand, HIGH);
}
void Screen_ILI9340::_writeData16(uint16_t data16)
{
    digitalWrite(_pinScreenDataCommand, HIGH);
    digitalWrite(_pinScreenCS, LOW);
    SPI.transfer(highByte(data16));
    SPI.transfer(lowByte(data16));
    digitalWrite(_pinScreenCS, HIGH);
}
void Screen_ILI9340::_writeData8(uint8_t data8)
{
    digitalWrite(_pinScreenCS, LOW);
    SPI.transfer(data8);
    digitalWrite(_pinScreenCS, HIGH);
}
void Screen_ILI9340::_writeData88(uint8_t dataHigh8, uint8_t dataLow8)
{
    digitalWrite(_pinScreenCS, LOW);
    SPI.transfer(dataHigh8);
    SPI.transfer(dataLow8);
    digitalWrite(_pinScreenCS, HIGH);
}
void Screen_ILI9340::_writeRegister16(uint8_t command8, uint16_t data16)
{
    _writeCommand8(command8);
 _writeData88(highByte(data16), lowByte(data16));
}
void Screen_ILI9340::_writeRegister8(uint8_t command8, uint8_t data8)
{
    _writeCommand8(command8);
 _writeData8(data8);
}
void Screen_ILI9340::_setPoint(uint16_t x1, uint16_t y1, uint16_t colour)
{
    _setWindow(x1, y1, x1, y1);
    _writeData88(highByte(colour), lowByte(colour));
}
void Screen_ILI9340::_setWindow(uint16_t x1, uint16_t y1, uint16_t x2, uint16_t y2)
{
    if (x1>x2) _swap(x1, x2);
    if (y1>y2) _swap(y1, y2);
    _writeCommand8(ILICASET);
    _writeData16(x1);
    _writeData16(x2);
    _writeCommand8(ILIPASET);
    _writeData16(y1);
    _writeData16(y2);
    _writeCommand8(ILIRAMWR);
}
void Screen_ILI9340::_fastFill(uint16_t x1, uint16_t y1, uint16_t x2, uint16_t y2, uint16_t colour)
{
    if (x1 > x2) _swap(x1, x2);
    if (y1 > y2) _swap(y1, y2);
    _setWindow(x1, y1, x2, y2);
    uint8_t hi = highByte(colour);
    uint8_t lo = lowByte(colour);
    for (uint32_t t=(uint32_t)(y2-y1+1)*(x2-x1+1); t>0; t--) {
        _writeData88(hi, lo);
    }
}
uint16_t Screen_ILI9340::readPixel(uint16_t x1, uint16_t y1)
{
    return 0;
}
void Screen_ILI9340::clear(uint16_t colour)
{
    uint8_t oldOrientation = _orientation;
    bool oldPenSolid = _penSolid;
    setOrientation(0);
    setPenSolid();
    rectangle(0, 0, screenSizeX()-1, screenSizeY()-1, colour);
    setOrientation(oldOrientation);
    setPenSolid(oldPenSolid);
}
void Screen_ILI9340::setOrientation(uint8_t orientation)
{
    _orientation = orientation % 4;
    _setOrientation(_orientation);
}
uint8_t Screen_ILI9340::getOrientation()
{
    return _orientation;
}
uint16_t Screen_ILI9340::screenSizeX()
{
    switch (_orientation) {
        case 0:
        case 2:
            return _screenWidth;
            break;
        case 1:
        case 3:
            return _screenHeigth;
            break;
    }
}
uint16_t Screen_ILI9340::screenSizeY()
{
    switch (_orientation) {
        case 0:
        case 2:
            return _screenHeigth;
            break;
        case 1:
        case 3:
            return _screenWidth;
            break;
    }
}
uint16_t Screen_ILI9340::screenDiagonal()
{
    return _screenDiagonal;
}
void Screen_ILI9340::circle(uint16_t x0, uint16_t y0, uint16_t radius, uint16_t colour)
{
    int16_t f = 1 - radius;
    int16_t ddF_x = 1;
    int16_t ddF_y = -2 * radius;
    int16_t x = 0;
    int16_t y = radius;
    if (_penSolid == false) {
        point(x0, y0+radius, colour);
        point(x0, y0-radius, colour);
        point(x0+radius, y0, colour);
        point(x0-radius, y0, colour);
        while (x<y) {
            if (f >= 0) {
                y--;
                ddF_y += 2;
                f += ddF_y;
            }
            x++;
            ddF_x += 2;
            f += ddF_x;
            point(x0 + x, y0 + y, colour);
            point(x0 - x, y0 + y, colour);
            point(x0 + x, y0 - y, colour);
            point(x0 - x, y0 - y, colour);
            point(x0 + y, y0 + x, colour);
            point(x0 - y, y0 + x, colour);
            point(x0 + y, y0 - x, colour);
            point(x0 - y, y0 - x, colour);
        }
    } else {
        while (x<y) {
            if (f >= 0) {
                y--;
                ddF_y += 2;
                f += ddF_y;
            }
            x++;
            ddF_x += 2;
            f += ddF_x;
            line(x0 + x, y0 + y, x0 - x, y0 + y, colour);
            line(x0 + x, y0 - y, x0 - x, y0 - y, colour);
            line(x0 + y, y0 - x, x0 + y, y0 + x, colour);
            line(x0 - y, y0 - x, x0 - y, y0 + x, colour);
        }
        setPenSolid(true);
        rectangle(x0-x, y0-y, x0+x, y0+y, colour);
    }
}
void Screen_ILI9340::line(uint16_t x1, uint16_t y1, uint16_t x2, uint16_t y2, uint16_t colour)
{
    if ((x1 == x2) && (y1 == y2)) {
        _setPoint(x1, y1, colour);
    } else if ((x1 == x2) || (y1 == y2)) {
        _fastFill(x1, y1, x2, y2, colour);
    } else {
        int16_t wx1 = (int16_t)x1;
        int16_t wx2 = (int16_t)x2;
        int16_t wy1 = (int16_t)y1;
        int16_t wy2 = (int16_t)y2;
        boolean flag = abs(wy2 - wy1) > abs(wx2 - wx1);
        if (flag) {
            _swap(wx1, wy1);
            _swap(wx2, wy2);
        }
        if (wx1 > wx2) {
            _swap(wx1, wx2);
            _swap(wy1, wy2);
        }
        int16_t dx = wx2 - wx1;
        int16_t dy = abs(wy2 - wy1);
        int16_t err = dx / 2;
        int16_t ystep;
        if (wy1 < wy2) ystep = 1;
        else ystep = -1;
        for (; wx1<=wx2; wx1++) {
            if (flag) _setPoint(wy1, wx1, colour);
            else _setPoint(wx1, wy1, colour);
            err -= dy;
            if (err < 0) {
                wy1 += ystep;
                err += dx;
            }
        }
    }
}
void Screen_ILI9340::dLine(uint16_t x0, uint16_t y0, uint16_t dx, uint16_t dy, uint16_t colour)
{
    line(x0, y0, x0+dx-1, y0+dy-1, colour);
}
void Screen_ILI9340::setPenSolid(bool flag)
{
    _penSolid = flag;
}
void Screen_ILI9340::point(uint16_t x1, uint16_t y1, uint16_t colour)
{
    _setPoint(x1, y1, colour);
}
void Screen_ILI9340::rectangle(uint16_t x1, uint16_t y1, uint16_t x2, uint16_t y2, uint16_t colour)
{
    if (_penSolid == false) {
        line(x1, y1, x1, y2, colour);
        line(x1, y1, x2, y1, colour);
        line(x1, y2, x2, y2, colour);
        line(x2, y1, x2, y2, colour);
    } else {
        _fastFill(x1, y1, x2, y2, colour);
    }
}
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

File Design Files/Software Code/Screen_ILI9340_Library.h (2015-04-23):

///
/// @file       Screen_ILI9340_Library.h
/// @brief      Library header
/// @details ILI9225 screen library
/// @n
/// @n @b       Project LCD_screen Library Suite
/// @n @a       Developed with [embedXcode](http://embedXcode.weebly.com)
///
/// @author     Rei VILO
/// @author     http://embedXcode.weebly.com
/// @date       Feb 18, 2014
/// @version 101
///
/// @copyright (c) Rei VILO, 2013
/// @copyright Attribution-NonCommercial-ShareAlike 3.0 Unported (CC BY-NC-SA 3.0)
///
/// @n  Single license: Attribution-NonCommercial-ShareAlike 3.0 Unported (CC BY-NC-SA 3.0)
///
/// @see
/// *  Rob's Color LCD Booster Pack (320x240 with microSD card socket) in Store
/// @n  https://www.tindie.com/products/RobG/color-lcd-booster-pack-320x240-with-microsd-card-socket/
/// *  Rob's (Universal) Color LCD graphics library (2) Posted 12 September 2013 - 01:41 PM
/// @n  http://forum.43oh.com/topic/4352-universal-color-lcd-graphics-library-2/#entry39090
/// *   Fonts generated with MikroElektronika GLCD Font Creator 1.2.0.0
#if defined(MPIDE)
#include "WProgram.h"
#elif defined(DIGISPARK)
#include "Arduino.h"
#elif defined(ENERGIA)
#include "Energia.h"
#elif defined(MAPLE_IDE)
#include "WProgram.h"
#elif defined(CORE_TEENSY)
#include "WProgram.h"
#elif defined(WIRING)
#include "Wiring.h"
#elif defined(ARDUINO)
#include "Arduino.h"
#endif
#ifndef SCREEN_ILI9340_LIBRARY_RELEASE
#define SCREEN_ILI9340_LIBRARY_RELEASE 101
#define MAX_FONT_SIZE 1
#if (MAX_FONT_SIZE > 0)
#include "Terminal6e.h"
#if (MAX_FONT_SIZE > 1)
#include "Terminal8e.h"
#endif
#endif
#include "SPI.h"
#define colour_black    0b0000000000000000
#define colour_white    0b1111111111111111
#define colour_red      0b1111100000000000
#define colour_green    0b0000011111100000
#define colour_blue     0b0000000000011111
#define colour_yellow   0b1111111111100000
#define colour_cyan     0b0000011111111111
#define colour_orange   0b1111101111100000
#define colour_magenta  0b1111100000001111
#define colour_violet   0b1111100000011111
#define colour_grey     0b0111101111101111
#define colour_darkGrey 0b0011100111100111
#define colour_brown    0b0111100000000000
#define _pinScreenCS 2
#define _pinSDcardCS 13
#define _pinScreenReset 20
#define _pinScreenDataCommand 5
class Screen_ILI9340 {
public:
    Screen_ILI9340();
    void begin();
    String WhoAmI();
 
 
 
    void clear(uint16_t colour = colour_black);
 
 
 
 
    void setOrientation(uint8_t orientation);
    uint8_t getOrientation();
 
    uint16_t screenSizeX();
    uint16_t screenSizeY();
 
    uint16_t screenDiagonal();
    void circle(uint16_t x0, uint16_t y0, uint16_t radius, uint16_t colour);
    void line(uint16_t x1, uint16_t y1, uint16_t x2, uint16_t y2, uint16_t colour);
    void dLine(uint16_t x0, uint16_t y0, uint16_t dx, uint16_t dy, uint16_t colour);
    void setPenSolid(bool flag = true);
 
 
 
 
 
 
 
 
    void triangle(uint16_t x1, uint16_t y1, uint16_t x2, uint16_t y2, uint16_t x3, uint16_t y3, uint16_t colour);
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
